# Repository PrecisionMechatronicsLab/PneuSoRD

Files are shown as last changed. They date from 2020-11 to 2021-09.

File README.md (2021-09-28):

<!-- TODO 
- Add image backgrounds
- Check the alternate text on images
- Add paypal link
 -->

# Overview
A link to the paper can be found here: http://www.precisionmechatronicslab.com/wp-content/uploads/2021/09/PneuSoRD_Paper_Submission.pdf

PneuSoRD is available to be purchased from: http://www.precisionmechatronicslab.com/soft-robotics/
<p align="center">
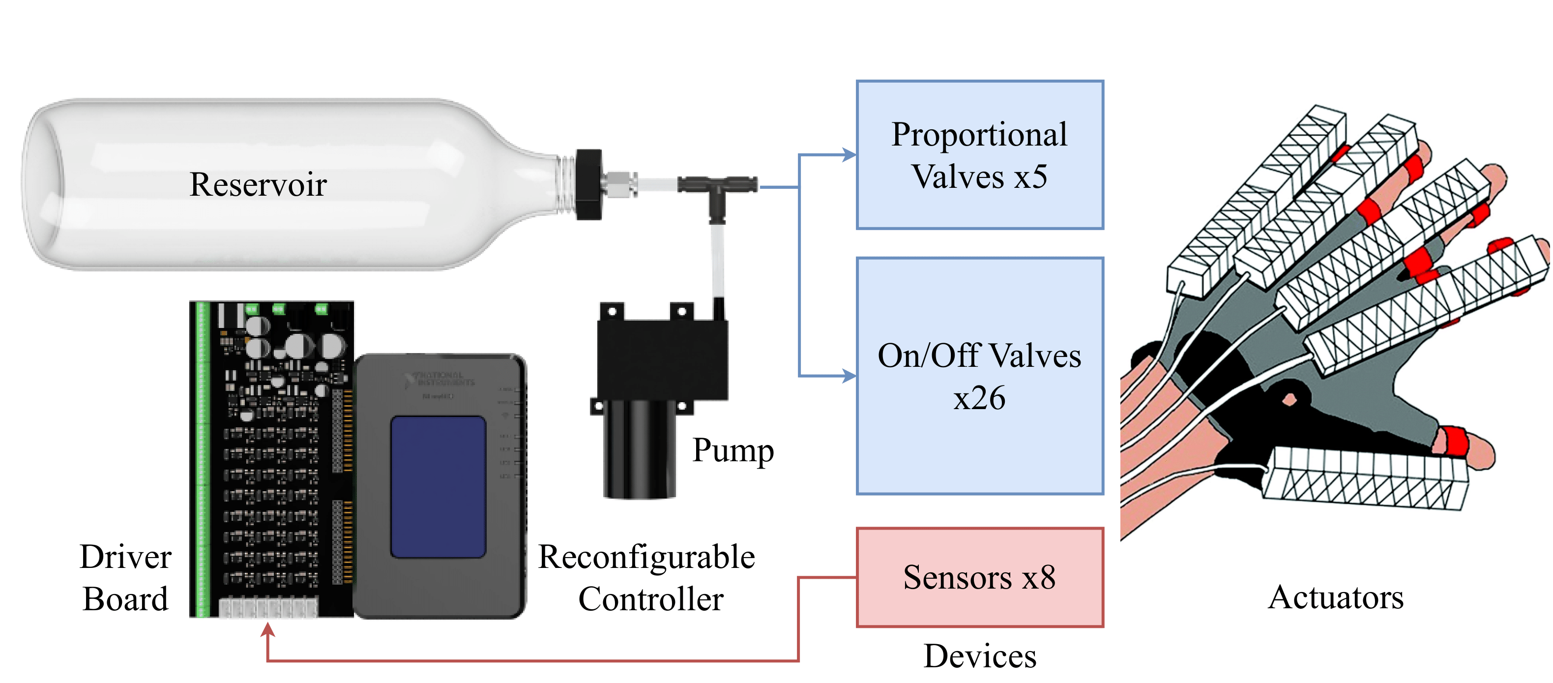
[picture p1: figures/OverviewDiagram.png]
Overview of the Pneumatic Soft Robotics Controller (PneuSoRD), including the electronics driver board and National Instruments myRIO controller, which is connected to a single pump and air receiver, up to 5 proportional valves, and 26 on-off valves. Soft robotic glove reproduced with permission fro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
	
</p>

The Pneumatic Soft Robotics Driver (PneuSoRD) is an open-source power electronics design for controlling pneumatic soft robotic actuators with a large number of simultaneous actuated chambers. This system is designed around the two major categories of valve types. On/Off valves with single or multiple solenoids which each take a binary input and proportional valves which can be driven from a variable DC voltage. Therefore, the PneuSoRD design encompasses a modular solution for each drive system: The "Proportional Drive" and the "On/Off Drive". Each module has been designed to be as generic as possible to allow control of a large range of valves with an available control strategy for each. These two modules can be driven by either a myRIO 1950 embedded controller through a real-time visual user interface with LabVIEW or an Arduino DUE.

**NOTE:** rev. 0.2 boards (unmarked revision) require the primary voltage input to be 7-12V. The secondary input can be used 7-25V.

## PneuSoRD Driver and Shield
The PneuSoRD can be replicated via the PCB_PneuSoRD files for use with the myRIO. An optional Arduino Due shield can also be made to adapt the PneuSoRD to an Arduino Due mirco controller.

<!-- TODO Add more information regarding build - brief summary of costs
Cost per unit for 20 units \~$160 -->

<!-- TODO Check these docs -->
https://github.com/PrecisionMechatronicsLab/PneuSoRD/blob/main/PCB_PneuSoRD/PCB_IC/PneuSoRD-BOM.xlsx
https://github.com/PrecisionMechatronicsLab/PneuSoRD/blob/main/PCB_DueAdapter/PCB_DueAdapterL2/Due-BOM.xlsx

# Quickstart Guide

The following guide is for the example [3 Way 2 Position](LabVIEW/3Way_2Position/OnOffControl_32Valve.vi) as seen in [On/Off 3/2](##On/Off-3/2).

### Step 1 - Pneumatic Connection
Connect the components as seen in Fig [On/Off 3/2](##On/Off-3/2). The specific fittings and components will vary depending on the valves and sensors used in your setup. 

### Step 2 - Pump/Valve Connections
Connect the two leads of the DC pump/motor to the Motor +- screw terminals.

For the 3/2 example connect the two leads of the valve to the +- of the desired channel, the example code utilises SO1, however this can be changed.

Connect the wall wart or power supply to the V2 power input of the driver via the DC barrel jack or the screw terminals. This supply should be selected based on the operating voltage of the motor/valves used. If these are the same, only one supply is needed, if they are different a second power supply can be connected to the V1 DC barrel jack or screw terminals. 

Using a pin jumper connect each devices controller to the appropriate power supply for that device. The right pin is used for V1 and the left for V2.

**NOTE:** rev. 0.2 boards (unmarked revision) require the primary voltage input to be 7-12V. The secondary input can be used 7-25V.

### Step 3 - Sensor Input
Connect the analogue sensor connectors to the headers marked AIX on the PCB.
For the example 3/2 on/off AI1 Pump, AI2 Actuator.

### Step 4 - LabVIEW Configuration
For each device configure the correct myRIO port.

Double clicking on the IO block for each device allows the user to configure the pin which the block reads/writes to and from. Set the pump, valve and sensors to use the myRIO pins which collorate to the driver pins. See tables [MXP A](#MXP-A) and [MXP B](#MXP-B) for the correct pin.

<p align="center">
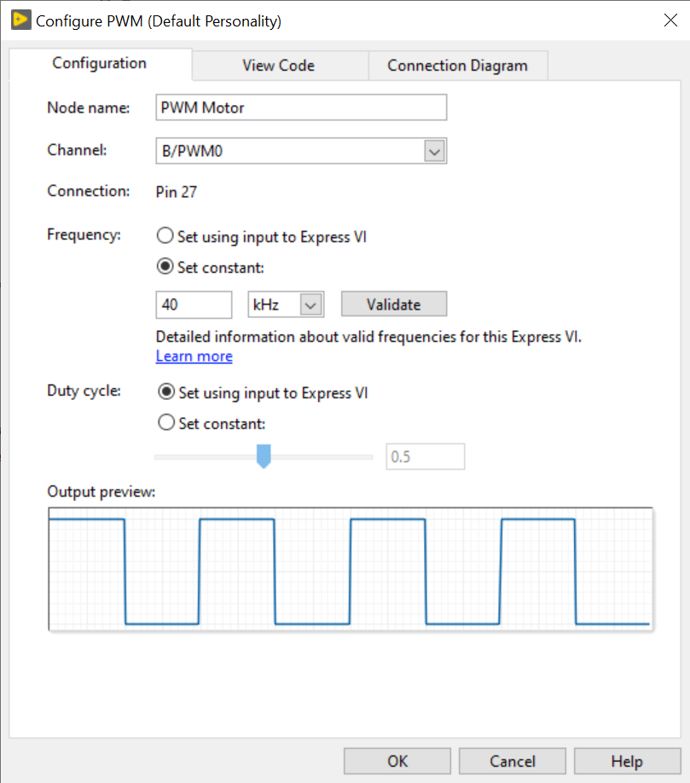
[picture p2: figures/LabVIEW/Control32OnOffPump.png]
LabView Control32OnOffPump interface
	
</p>

<p align="center">3/2 on-off pump configuration</p>

<p align="center">
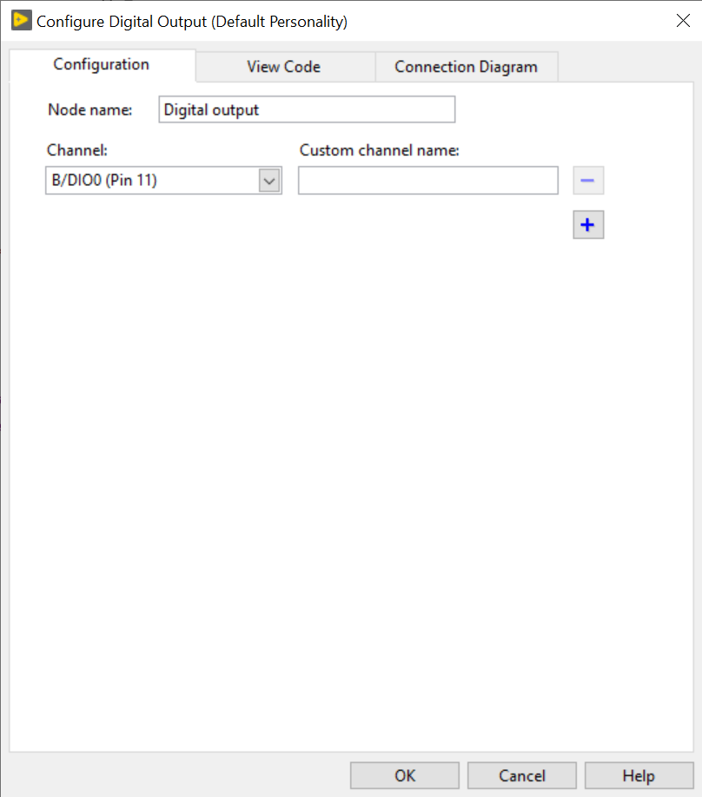
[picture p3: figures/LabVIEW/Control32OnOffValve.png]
LabView Control32OnOffValve interface
	
</p>

<p align="center">3/2 on-off valve configuration</p>

<p align="center">
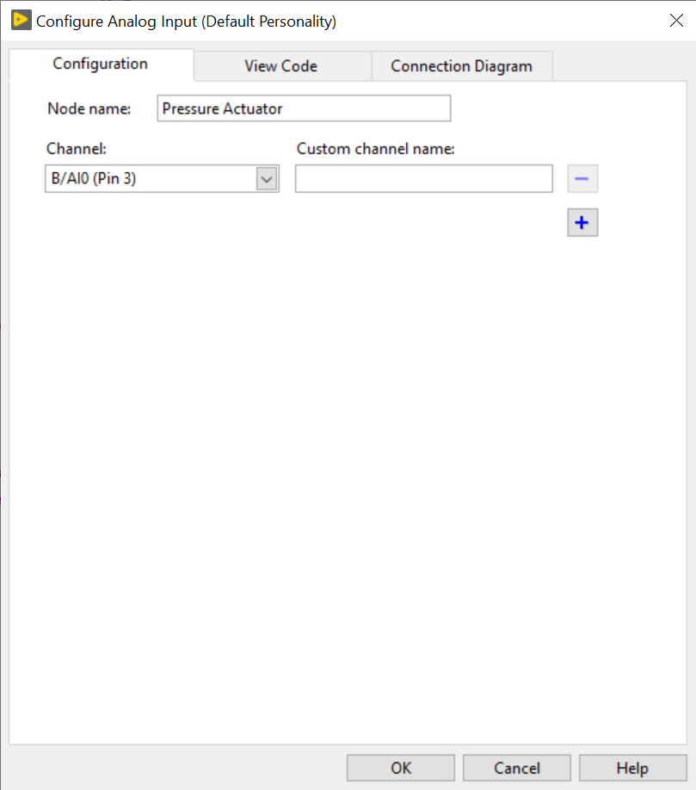
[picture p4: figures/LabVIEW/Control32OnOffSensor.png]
LabView Control32OnOffSensor interface
	
</p>

<p align="center">3/2 on-off sensor</p>

### Step 5 - Running the LabVIEW vi
Once the configuration is complete, the system is ready to test. Use the *run* and *Abort Execution* buttons to control the device. 

The "Setpoint Receiver" slider allows the resivour pressure (kPa) to be adjusted. The limit for this pressure is dependent on the resivour and pump used.

The second slider "Setpoint Actuator" adjusts the desired actuator pressure. 

For each slider there is an associated "Performance" guage. The *red* needle displays the setpoint direct from the slider and the *black* needle displays the measured pressure.

<!-- TODO Talk about the control view -->
<p align="center">
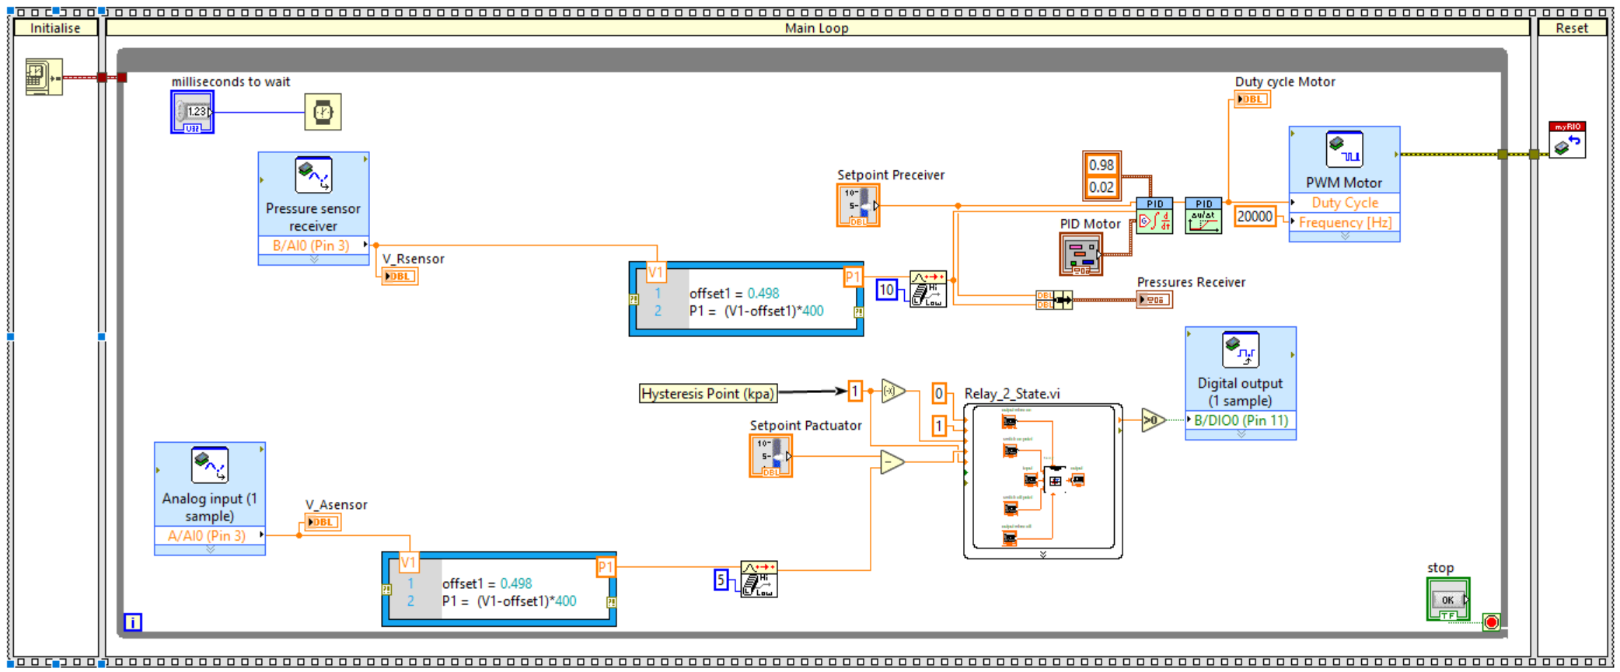
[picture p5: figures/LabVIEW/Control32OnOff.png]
	
</p>

<!-- TODO Talk about the interface view -->
<p align="center">
	LabView control interface 3/2 On/Off
</p>

Table of contents
=================
<!-- TODO Update TOC -->
<!--ts-->
   * [Overview](#Overview)
   * [Quickstart Guide](#Quickstart-Guide)
   * [PneuSoRD Driver](#PneuSoRD-Driver)
   * [Pnuematic Overview](#Pnuematic-Overview)
	 * [Pump/Compressor ](#Pump/Compressor )
	 * [3/2 Valve Configuration](#3/2-Valve-Configuration)
	 * [3/3 Valve Configuration](#3/3-Valve-Configuration)
	 * [2x 2/2 Valve Configuration](#2x-2/2-Valve-Configuration)
   * [LabVIEW Overview](#LabVIEW-Overview)
	 * [Main Loop](#Main-Loop)
	 * [Analog Input](#Analog-Input)
	 * [PWM](#PWM)
	 * [Simulated Squarewave](#Simulated-Squarewave)
	 * [Digital Write](#Digital-Write)
	 * [PID Block](#PID-Block)
	 * [Relay Block](#Relay-Block)
	 * [Rate Limiter Block](#Rate-Limiter-Block)
   * [Control Implementations](#Control-Implementations)
	 * [Pump Control](#Pump-Control)
	 * [On/Off 3/2](#On/Off-3/2)
		 * [Bang-Bang](#Bang-Bang)
		 * [PID](#PID)
	 * [On/Off 2x 2/2](##On/Off-2x-2/2)
		 * [Bang-Bang](#Bang-Bang)
		 * [PID](#PID)
	 * [Proportional 3/2](#Proportional-3/2)
	 * [Proportional 2x 2/2](#Proportional-2x-2/2)
   * [Hardware Overview](#Hardware-Overview)
	 * [Electrical Design (PneuSoRD)](#Electrical-Design-(PneuSoRD))
		 * [Motor/Proportional Drive](#Motor/Proportional-Drive)
		 * [On/Off Drive](#On/Off-Drive)
		 * [Sensor Input](#Sensor-Input)
	 *  [Arduino Sheild](#Arduino-Shield)
	 * [Pin Mapping](#Pin-Mapping)
		 * [MXP A](#MXP-A)
		 * [MXP B](#MXP-B)
<!--te-->

# Pnuematic Overview
An overview of pneumatic configurations.

## Pump/Compressor 
<p align="center">
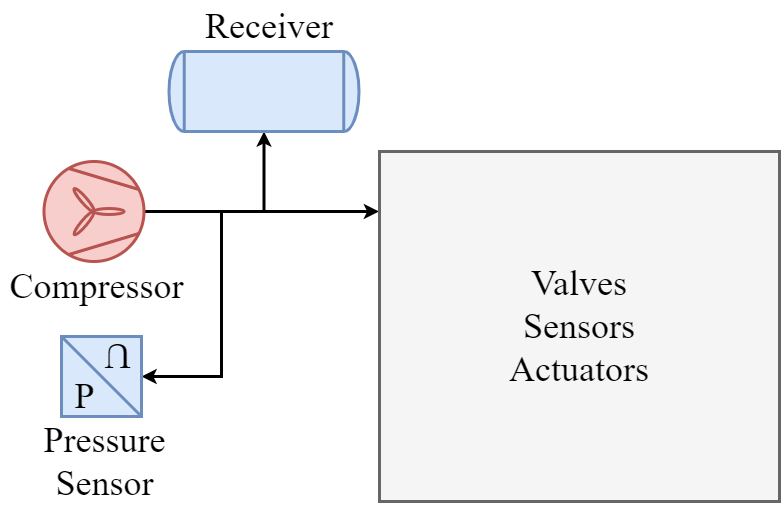
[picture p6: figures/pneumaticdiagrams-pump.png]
Air compressor with reservoir and pressure sensor
	
</p>

The main components of a compressed air system are the pump or source, an optional accumulator and an inline pressure sensor. The addition of an air receiver (storage reservoir or gas tank) to the pneumatic system smooths pulsating flow and prevents excessively temporary pressure drop during sudden short-term demand. Moreover, the air receiver allows for reduced energy consumption and fast pressurization of soft actuators.

## 3/2 Valve Configuration
<p align="center">
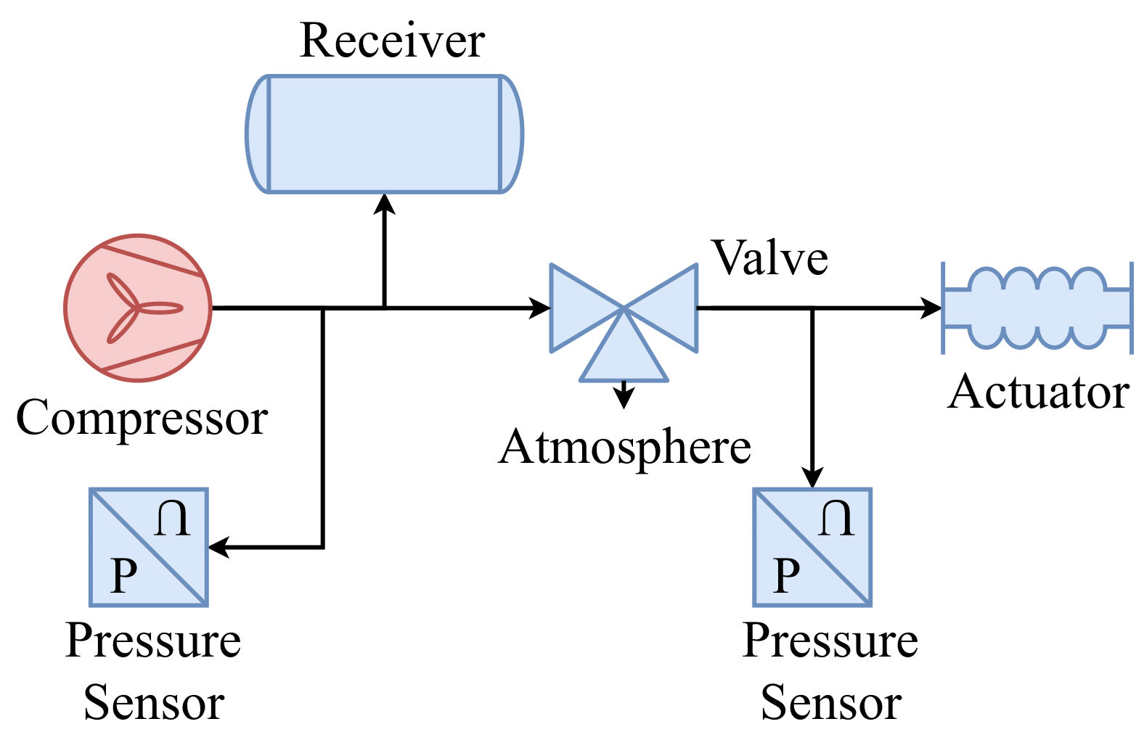
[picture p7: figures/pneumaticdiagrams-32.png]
Pneumatic system with a 3/2 valve coniguration
	
</p>

For the 3/2 valve system as shown above, the inlet port is connected to the compressor or the receiver, the outlet port is connected to the soft actuator and the exhaust port is open to atmosphere. The 3/2 valve system implies constantly inflating and deflating each pneumatic chamber, which causes the pressure in the actuator to continuously oscillate around its target and potentially reduces the lifetime of the valves.

## 3/3 Valve Configuration
<p align="center">
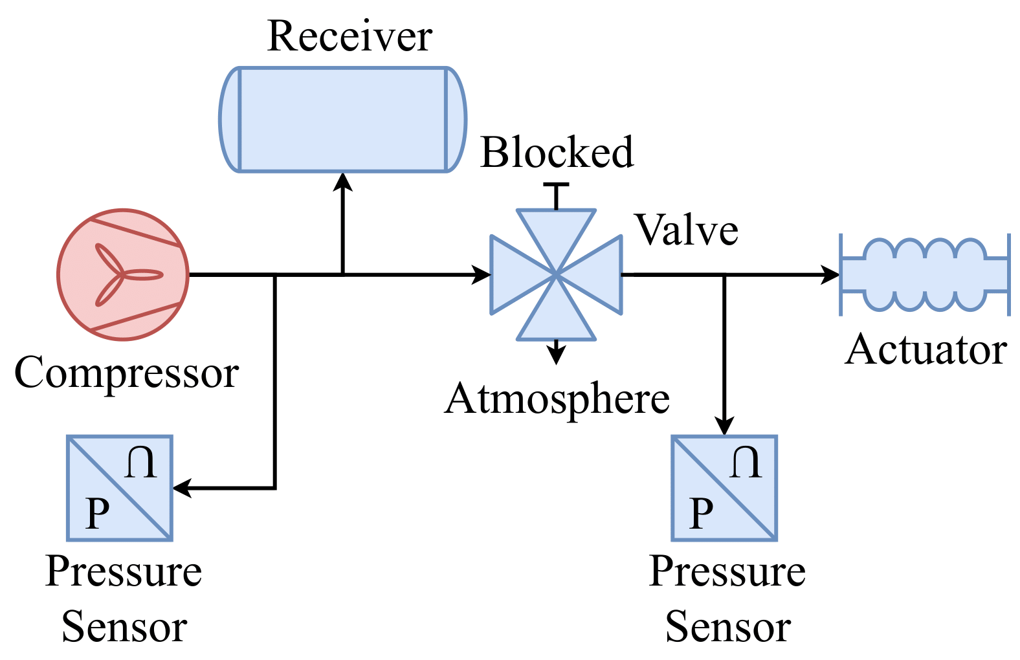
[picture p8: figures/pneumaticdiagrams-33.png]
Pneumatic system with a 3/3, 4/3 or 5/3 valve coniguration.
	
</p>

For the 3/3, 4/3 or 5/3 valve system as shown above, the inlet port is connected to the compressor or the receiver, the outlet port is connected to the soft actuator and the exhaust port is open to atmosphere. These valve systems have both inflating, deflating and holding modes.

## 2x 2/2 Valve Configuration
<p align="center">
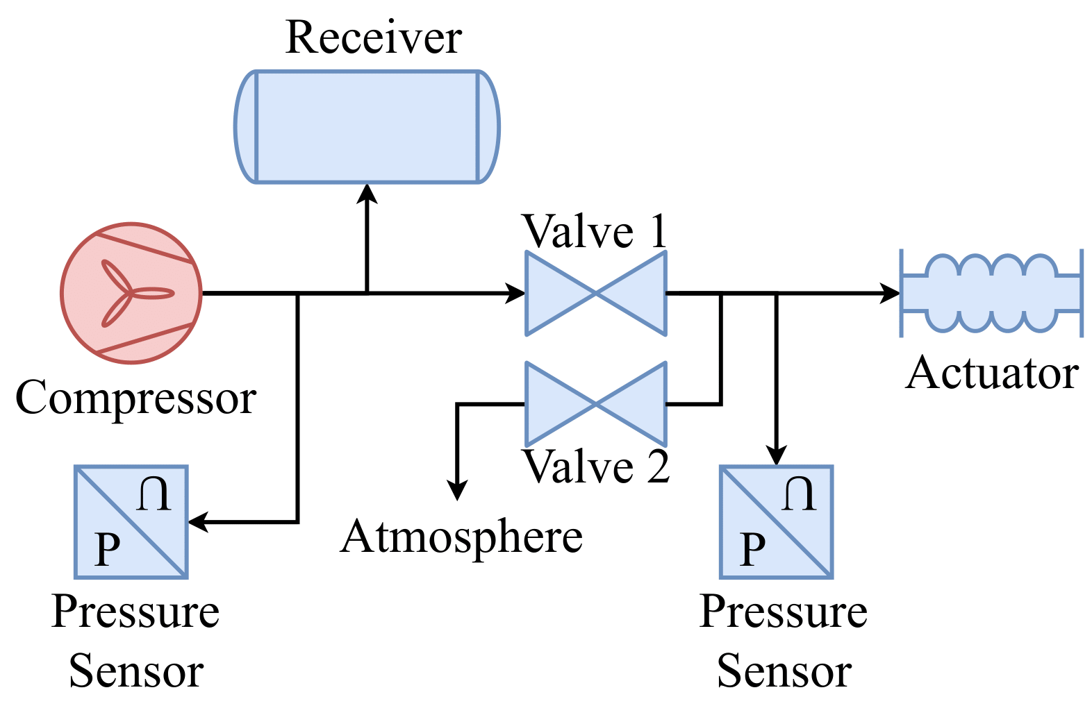
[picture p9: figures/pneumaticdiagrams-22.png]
Pneumatic system with 2x 2/2 valve coniguration
	
</p>

For the system with two 2/2 valves, the first valve is responsible for the charging process and has its inlet port connected to the compressor or the receiver and outlet port connected to the soft actuator. The second valve is responsible for the discharging process and has its inlet port connected to the soft actuator and outlet port open to atmosphere. Proportional valves outperform on-off solenoid valves in regards to tracking precision and steady-state accuracy but are 3-4 times more expensive.

# LabVIEW Overview
LabVIEW offers a graphical programming approach that helps you visualize every aspect of your application, including hardware configuration, measurement data, and debugging. This visualization makes it simple to design and develop custom engineering user interfaces.

Below is an overview of some of the major LabVIEW blocks used for a the outlined control configurations for the PneuSoRD.

## Installed packages

Download the 'LabVIEW 2019 myRIO Software Bundle' https://www.ni.com/en-au/support/downloads/software-products/download.labview-myrio-software-bundle.html and install these optional dependencies
-	JKI VI Package Manager
-	LabVIEW
-	LabVIEW myRIO Toolkit
-	LabVIEW Real-Time Module
-	LabVIEW Control Design and Simulation Module
-	LabVIEW MathScript Module
-	LabVIEW Robotics Module for LabRIO

## Main Loop
<p align="center">
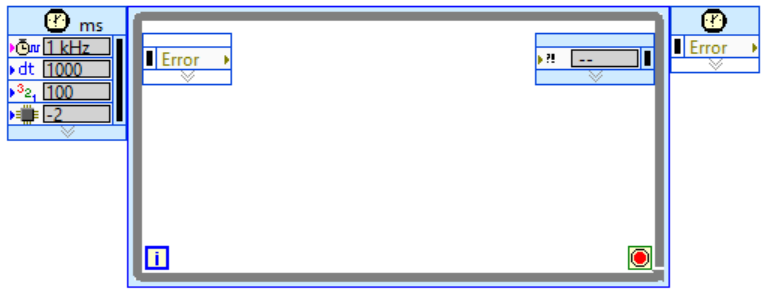
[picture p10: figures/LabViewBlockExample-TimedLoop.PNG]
LabView Timed Loop Block
	
</p>

The Timed Loop block  forms the foundation of the control system developed. All LabVIEW blocks are placed within this loop which determines the speed at which the control system runs. Whilst it is possible to replace this block with a While Loop, a fixed period is preferred. This block contains a parameter for setting the loop frequency or period.

## Analog Input
<p align="center">
	LabView Analog Input Block
</p>

This block reads the analog value of a single user predefined pin. This block contains no input functionality for use in the LabVIEW environment. The block outputs a 12bit analog value.

## PWM
<p align="center">
	LabView PWM Block
</p>

This block generates a hardware PWM signal to a single user predefined pin. The inputs to this block are the PWM duty cycle and PWM frequency. This block contains no output functionality for use in the LabVIEW environment.

## Simulated Squarewave
<p align="center">
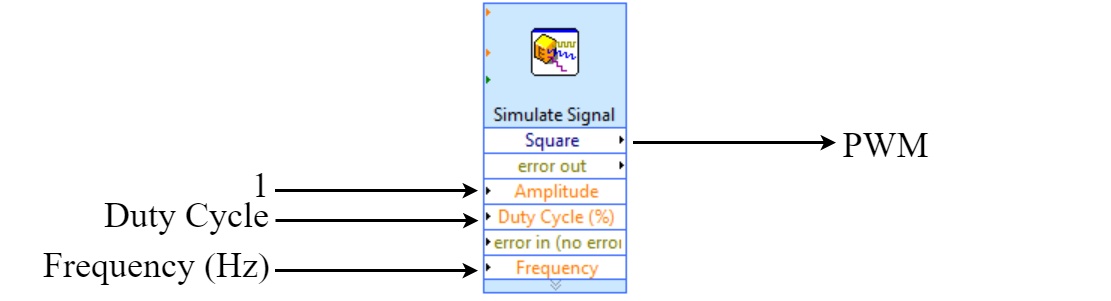
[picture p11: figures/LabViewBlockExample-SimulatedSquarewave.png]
LabView Simulated Squarewave Block
	
</p>

This block generates a wave function defined by the user. For this application a squarewave has been selected to mimic a PWM signal. The inputs to this block are the amplitude of the signal (for PWM generation this is 1), PWM duty cycle and PWM frequency. This block outputs the state of the Simulated wave at each loop itteration. 

## Digital Write
<p align="center">
	LabView Digital Write Block
</p>

This block allows the user to set the state of a single user predefined pin. The input to this block is the binary pin state. This block contains no output functionality for use in the LabVIEW environment. When used in conjunction with the Simulated Squarewave block this can be used to generate a software PWM signal.

## PID Block
<!-- TODO Add this image -->
<p align="center">
	LabView PID Block
</p>

This block implements a standard PID controller with P gain, I gain and D gain controls. The input to this block is the driving error signal. The output for this block is the driving control signal.

## Relay Block
<p align="center">
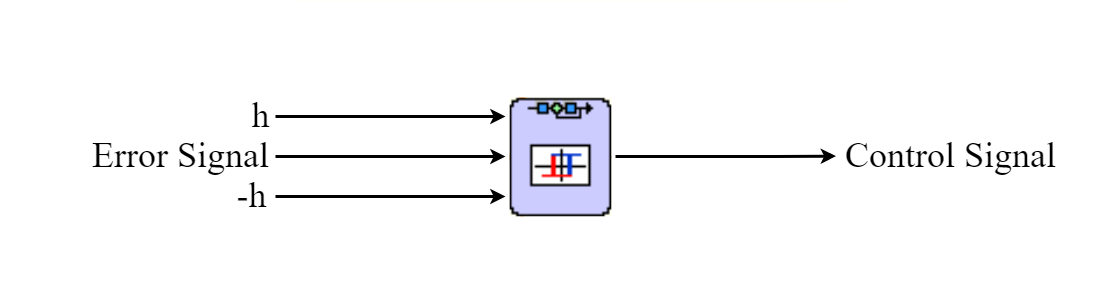
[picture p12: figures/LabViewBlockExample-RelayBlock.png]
LabView Relay Block
	
</p>

This block can be used to create a hysteresis window with two states. The inputs to this block are the maximum and minimum crossing point for the window and the driving error signal. The output to this block is the binary state of the signal.

<p align="center">
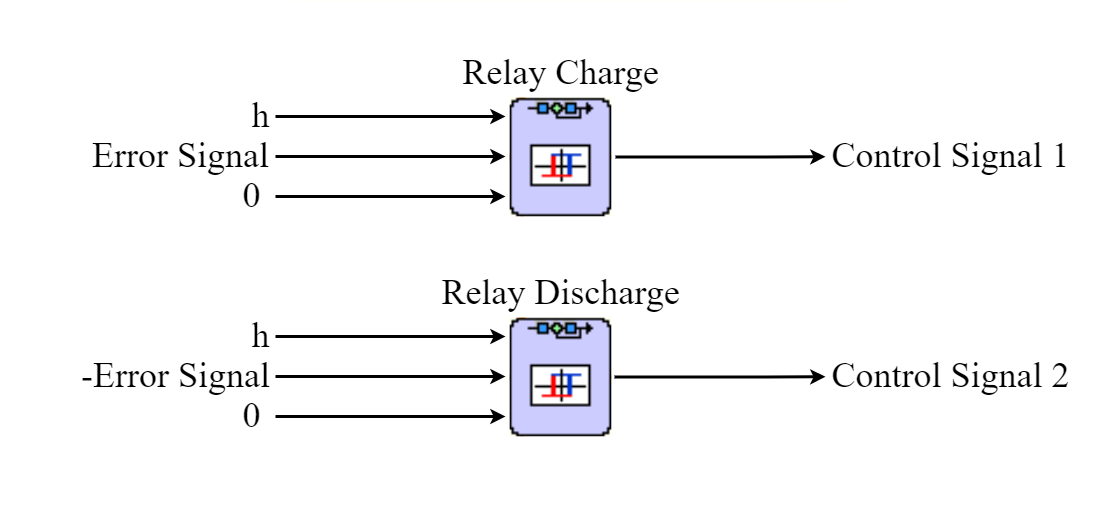
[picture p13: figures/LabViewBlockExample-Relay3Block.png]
LabView 3 State Relay Block
	
</p>

When combined with a second relay block, a three state hysteresis window can be implemented. The block inputs are the maximum, minimum and middle crossing point for the windows and the driving error signal. The output to this block is a pair of binary states for each window.

## Rate Limiter Block
<p align="center">
	LabView Rate Limiter Block
</p>

This block limits the rate of change over time of the input signal. The input to this block is the signal to be rate limited. The output to this block is the rate limited signal.

# Control Implementations
The following section decribes a control implementation for each valve type. Each of these control implementations are available in the repository above.

## Pump Control

The accumulator pressure requires closed-loop control to provide a constant source pressure. This is achieved by controlling the motor voltage by regulating the duty cycle using a PID controller.

<p align="center">
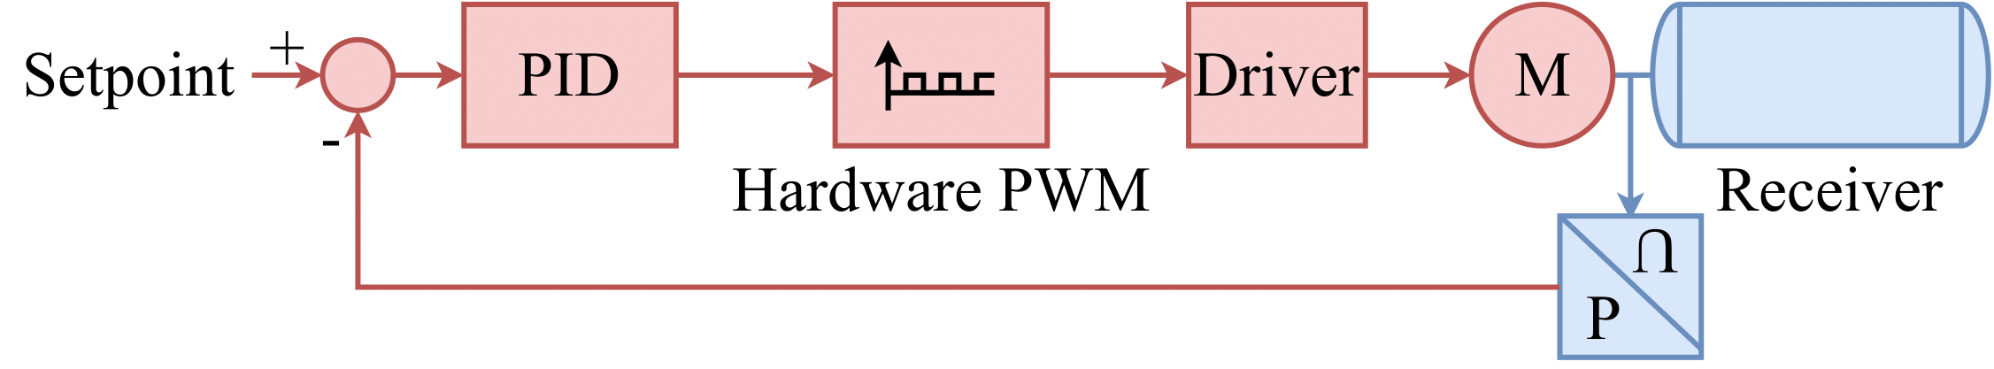
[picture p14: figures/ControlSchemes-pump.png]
Motor driver control scheme
	 
</p>

## On/Off 3/2
### Bang-Bang

For the system with a 3/2 on-off valve, the bang-bang controller is implemented with two states, which are:

<p align="center">
P < P_ref - h  
P > P_ref + h 
</p>

where **P** is the measured pressure, **P_ref** is the reference pressure and **h** is half the size of the hysteresis band. Lower values of hysteresis result in less steady-state error but also higher switching frequency. These conditions are implemented by using a relay block in Simulink or a relay function in a subsystem in LabVIEW with "switch on point" equal to **h** and "switch off point" equal to **-h**. Note that hysteresis is introduced for the bang-bang controllers to prevent excessive switching, which is particularly beneficial for the systems with 2/2 valves.

<p align="center">
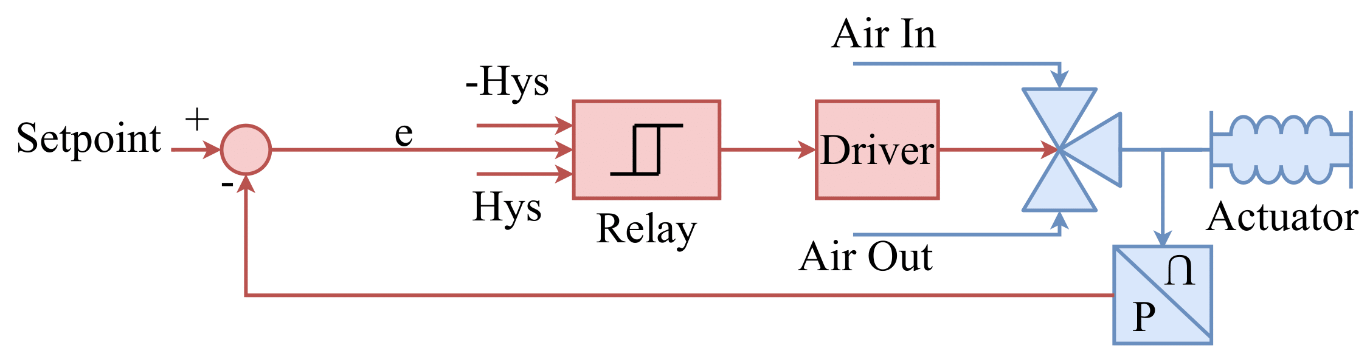
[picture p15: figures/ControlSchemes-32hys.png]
	 
</p>

### PID

For the system with a 3/2 on-off valve, the PID controller is implemented by regulating the duty cycle of the PWM wave into the valve between zero and 100%, which is used to switch the valve continuously between two states at a fixed frequency, e.g. 40Hz.

<p align="center">
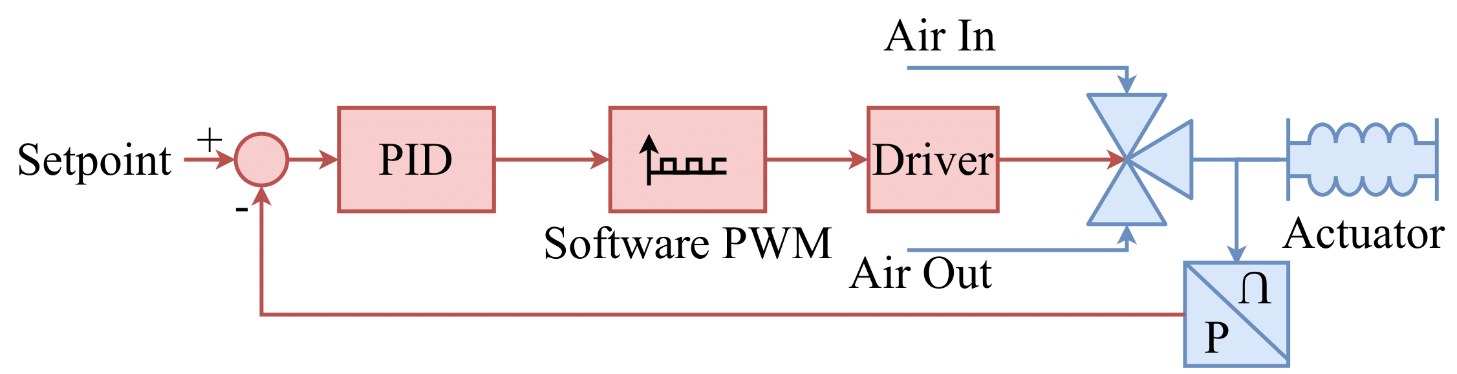
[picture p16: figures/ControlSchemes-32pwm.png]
3/2 on-off valve system with PID controller
	 
</p>

## On/Off 2x 2/2
For the system with two 2/2 on-off valves, the first valve (control **u_1**) is used for charging by allowing air flow from the receiver into the actuator. The second valve (control **u_2**) is used for discharging by allowing flow from the actuator into atmosphere.
### Bang-Bang

The bang-bang controller, three states can be used. In the first state, valve 1 is used for charging the actuator while valve 2 is blocked, i.e. **u_1 = 1** and **u_2 = 0**. In the second state, both valves are blocked and no flow is allowed from the receiver or into the atmosphere, i.e. **u_1 = 0** and **u_2 = 0**. Finally, in the third state, valve 2 is used to discharge the actuator into the atmosphere while valve 1 is blocked, i.e. **u_1 = 0** and **u_2 = 1**. These conditions can be implemented using a case structure (state machine) with three states or by considering the logic below with two relays.

Valve 1

* Switch on: P_ref - P > h

* Switch off: P_ref - P = 0

Valve 2

* Switch on: P_ref - P < -h

* Switch off: P_ref - P = 0

<p align="center">
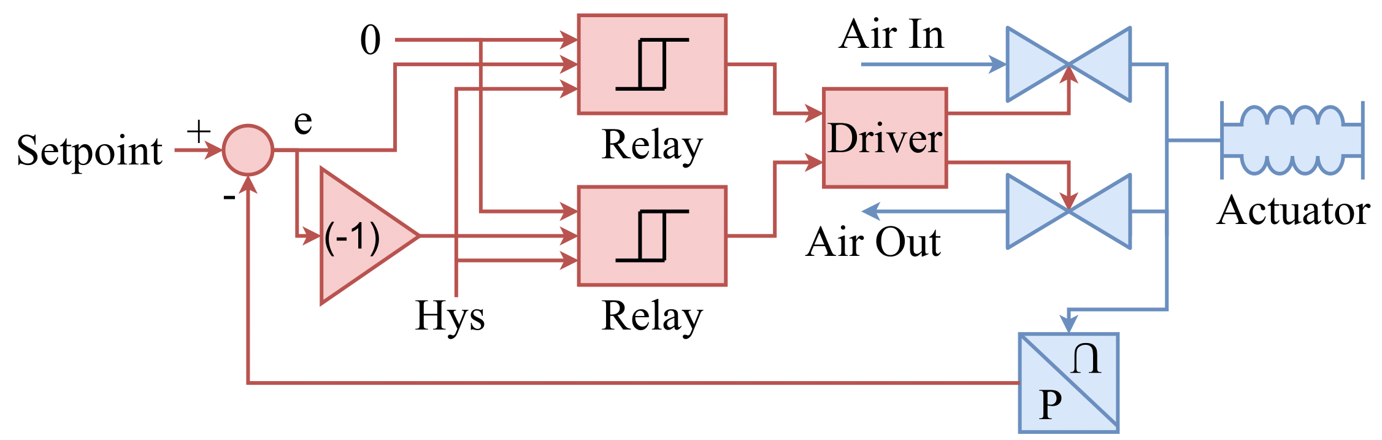
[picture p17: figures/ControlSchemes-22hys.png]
2x 2/2 on-off valve system with bang-bang controller
	 
</p>

### PID

The PID controller is implemented by regulating the duty cycle of complementary PWM signals at a fixed frequency.

<p align="center">
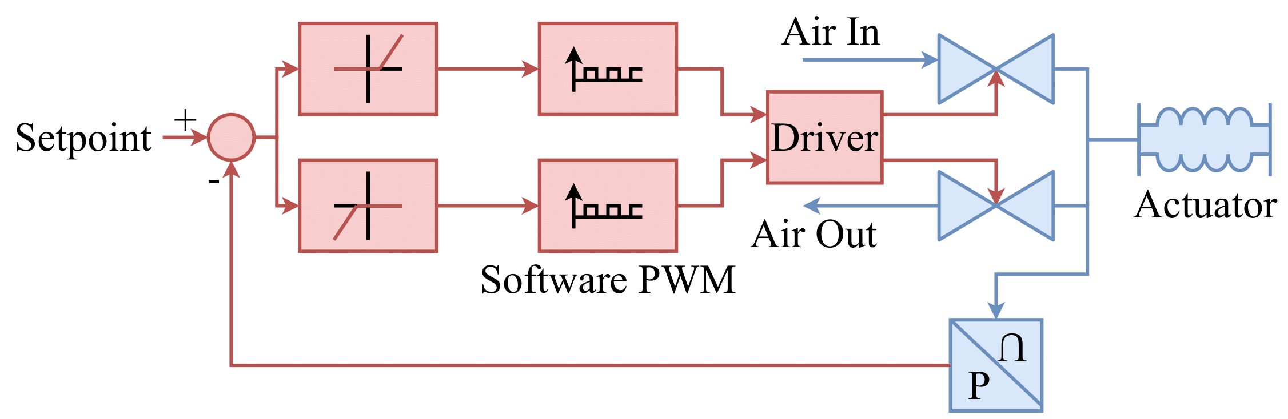
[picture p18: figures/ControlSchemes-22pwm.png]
2x 2/2 on-off valve system with PID controller
	 
</p>

## Proportional 2x 2/2

For 2/2 proportional valves, the mapping from input voltage to output flow is approximately linear over the operating range. A small deadband can be implemented for each valve around the zero error point. Outside of this region a linear mapping between error and duty cycle can be produced to regulate the pressure in the system. Alternatively, the use of a bang-bang controller would not be recommended, as this would effectively be treating the proportional valve as a two state on/off valve.

<p align="center">
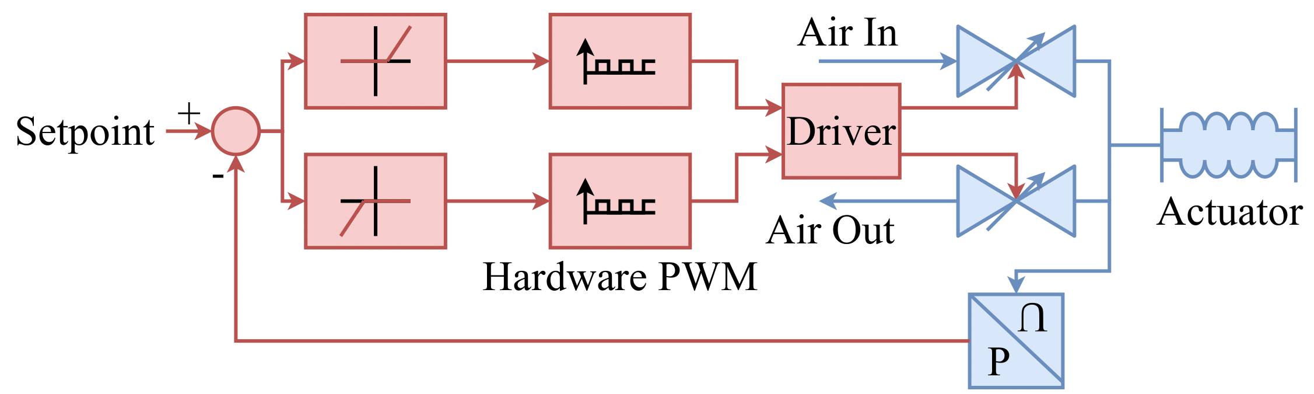
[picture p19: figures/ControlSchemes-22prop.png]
Proportional PWM driver with PID controller
	 
</p>

# Hardware Overview
The driver allows for the control of up to 31 valves for use in a multitude of applications. The number of sensor inputs is limited according the maximum number of analog inputs of myRIO. Consequently, 8 sensors input headers can be used to perform independent feedback control on 8 chambers. Note that more chambers can be actuated if they are allowed to share the same pressure values. 
An electrical PWM is used to drivethe proportional valves through a buck converter, which produces the required DC voltage. Where as a pneumatic PWM is produces by switching on and off the supply to the On/Off valves to produce the required driving signal. The PneuSoRD has two power inputs each of which can supply an operating voltage 7-25V. Two inputs were chosen to maximise the range or valves that could be driven. The primary input is used to power the 5V regulator and is required for the board's protection functionality. Whilst the secondary input is only required if a second voltage level is needed.

**NOTE:** rev. 0.2 boards (unmarked revision) require the primary voltage input to be 7-12V. The secondary input can be used 7-25V.

As seen in the image below, the driver interfaces with the myRIO via the two IDC connectors on the left hand side of the myRIO. 
<p align="center">
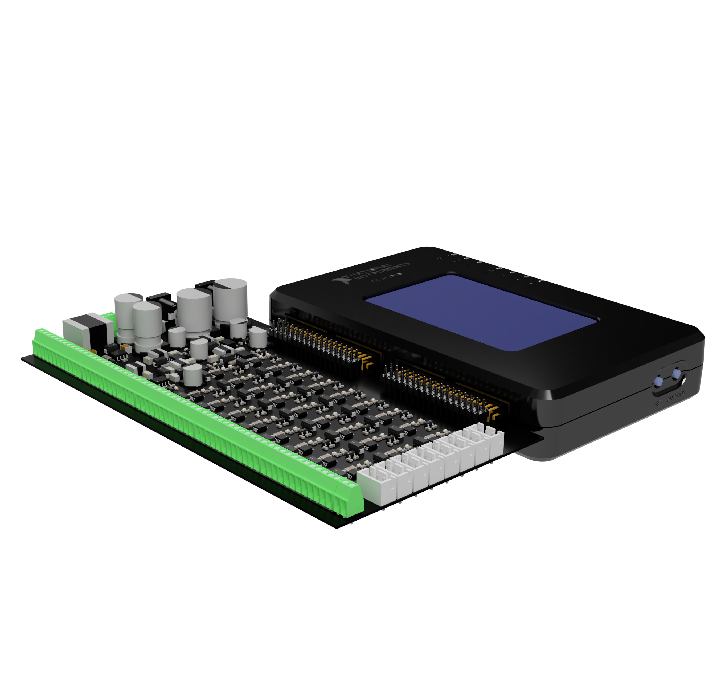
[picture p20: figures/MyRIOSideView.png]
MyRIO Side View
	
</p>

## Electrical Design (PneuSoRD)
Each module has been designed to maximise the variety of devices which can be driven. The following shows the implementation of the three drive designs and the feedback sensor electronics.  
<!-- <div class="text-red mb-2"> -->
Red - 26 On/Off Drives  
<!-- </div> -->
<!-- <div class="text-yellow mb-2"> -->
Yellow - 5 Proportional Drives
<!-- </div>   -->
<!-- <div class="text-blue mb-2"> -->
Blue - 1 Motor Drive  
<!-- </div> -->
<!-- <div class="text-green mb-2"> -->
Green - Power Supply  
<!-- </div> -->
<!-- <div class="text-orange mb-2"> -->
Orange - Sensor Inputs  
<!-- </div> -->
<!-- <div class="text-pink mb-2"> -->
Pink - Expansion Headers  
<!-- </div> -->

<p align="center">
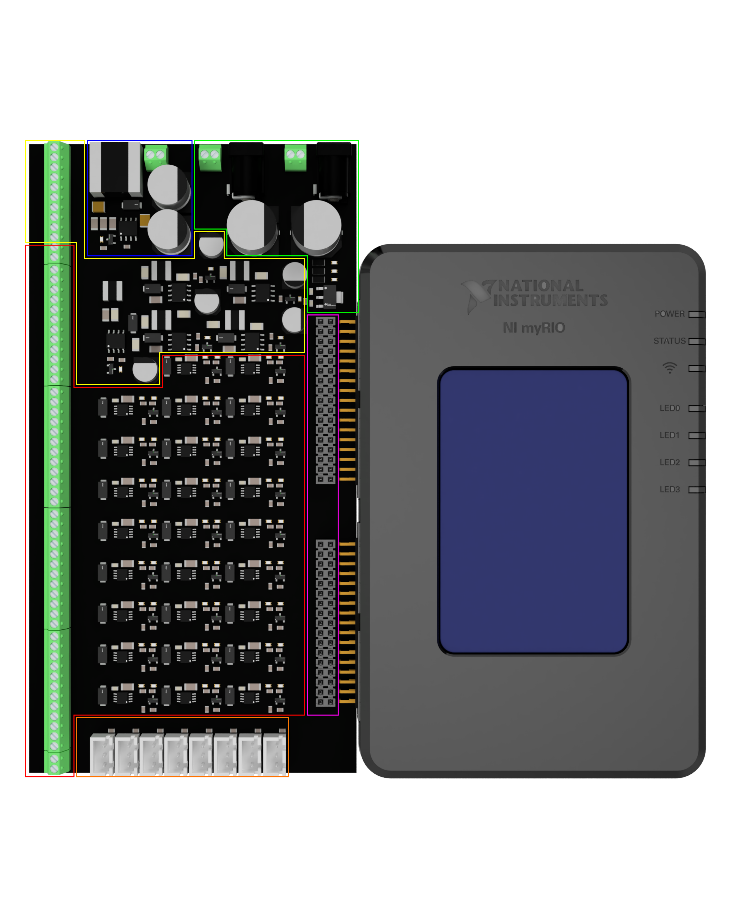
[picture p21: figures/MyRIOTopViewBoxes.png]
MyRIO Top View
	
</p>

### Motor/Proportional Drive
The PneuSoRD has 6 Proportional Drive modules. The motor driver is sized for a peak current up to 1.4A. This driver is designed for DC motor pumps that typically require a current of 500mA to 1A. This output could also be used to drive a logic signal for a larger pump. The 5 proportional drivers are sized for a peak current capacity up to 700mA. This driver is designed for driving proportional valves that typically require 200mA to 500mA.

The motor and proportional valve drivers are based off a synchronous rectifier buck converter. The switch is driven by a 40-200kHz PWM signal with a variable duty cycle, which can be generated by the myRIO or Arduino Due controllers. The switch (DRV88703.6A) is a half-bridge motor driver and was selected for the comprehensive overload protection, which is described in Section .

Each circuit channel can be supplied by either of two power supply inputs via a jumper on each circuit channel. The maximum output current is set by the **Rsen** resistor, which provides over-current and short-circuit protection. In the default configuration, the motor driver channel can supply 1.4A continuously and 2.5A peak, which is adjustable up to 3.6A. The remaining 5 proportional driver channels can supply 500mA continuously and 

### On/Off Drive
Since on-off valves can be driven by a digital signal, the PneuSoRD uses 26 digital pins on the myRIO and Arduino Due. The TPS1H000 is a fully protected single channel high-side power switch with an integrated power transistor. Each drive contains an adjustable current limit that can be adjusted via the **Rsen** resistor. This protection feature limits the inrush or overload current. The trip delay capacitor has been selected to minimise the trip time if a fault event occurs. A light emitting diode is connected to the fault pin, which provides user feedback during a fault condition.

Each drive channel can be supplied by either of the power supply inputs via a jumper on each channel. The on-off channels can supply 500mA continuously, with a peak of 500mA, which is adjustable up to 1A.

### Sensor Input
A total of 8 sensor input headers are included on the PneuSoRD, with an additional 4 included on the Arduino Due shield. A linear regulator provides each sensor with 5V, this reduces sensor noises caused by noise on the power rail due to the switching of the other components. Primarily, this input is designed for 0-5V sensors that can be read via the ADC input of the microcontroller. An optional resistor can be added to suit 4mA to 20mA style sensors.

## Arduino Shield
<!-- TODO add diagram of shield and overview -->
<p align="center">
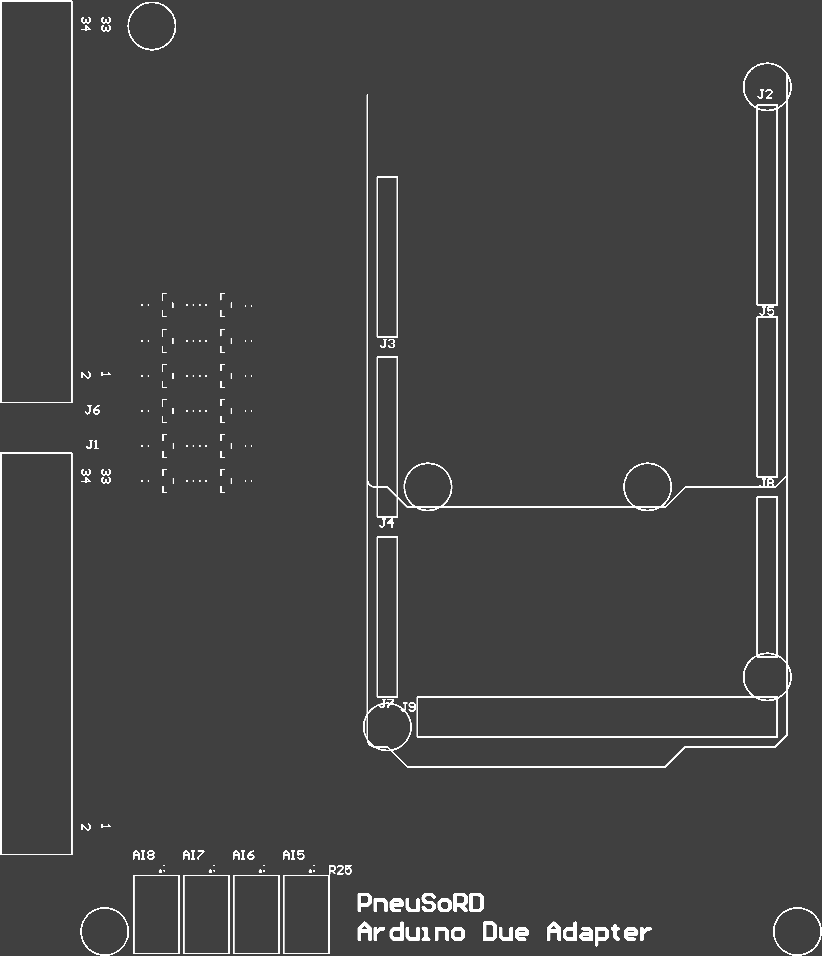
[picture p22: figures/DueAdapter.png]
Arduino Shield Render
	
</p>

## Pin Mapping
The pin mapping for the PneuSoRD integrates the two MXP connectors of the MyRIO. The table below presents the pin mapping as seen in the orientation of the PneuSoRD driver. This is also the orientation of the pins of the breakout header.

<p align="center">
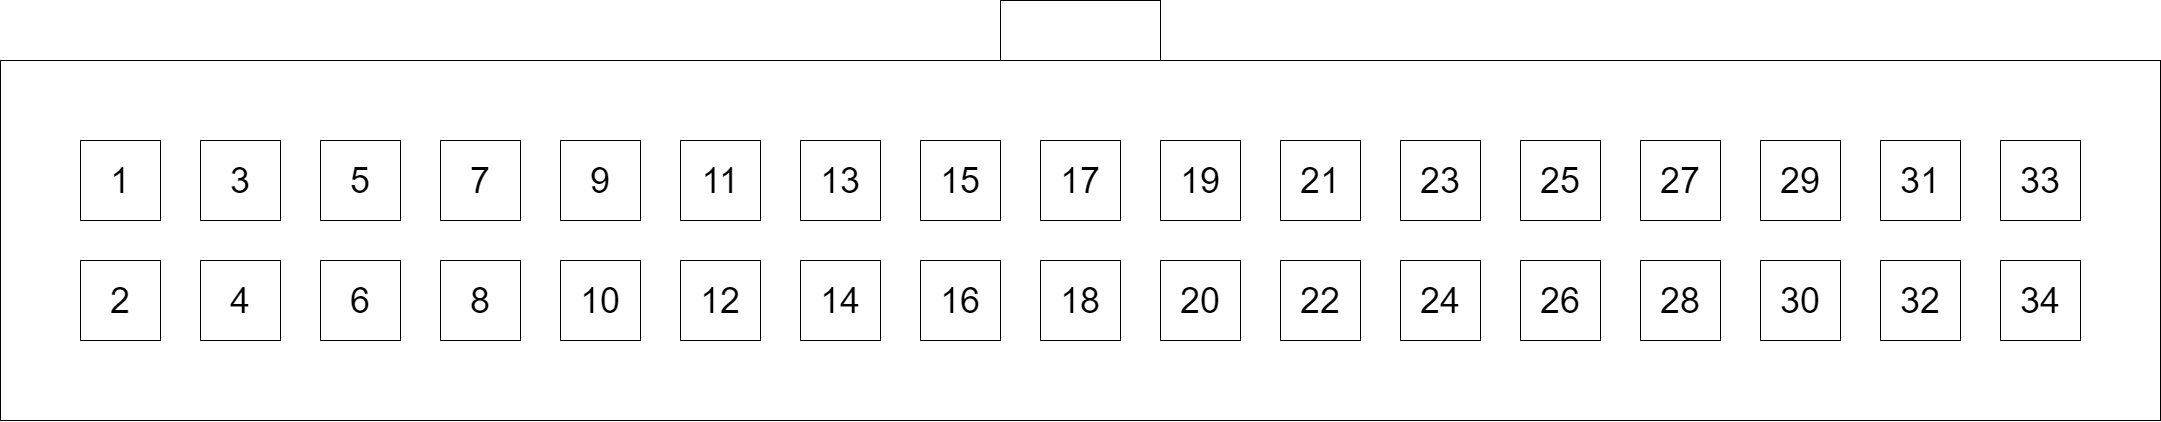
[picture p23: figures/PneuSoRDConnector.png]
MyRIO MXP Connector
	
</p>

### MXP A
| MyRIO Pin | MyRio Function | PneuSoRD Pin | MyRIO Pin | MyRio Function | PneuSoRD Pin | 
| ------ | ------ | ------ | ------ | ------ | ------ |
| MXP A Pin 34 | DIO15/I2C.SDA | SO26 | MXP A Pin 33 | +3.3V         | 3V3  |
| MXP A Pin 32 | DIO14/I2C.SCL | SO25 | MXP A Pin 31 | DIO10/PWM2    | P5   |
| MXP A Pin 30 | DGND          | GND  | MXP A Pin 29 | DIO9/PWM1     | P4   |
| MXP A Pin 28 | DGND          | GND  | MXP A Pin 27 | DIO8/PWM0     | P3   |
| MXP A Pin 26 | DIO13         | SO24 | MXP A Pin 25 | DIO7/SPI.MOSI | SO23 |
| MXP A Pin 24 | DGND          | GND  | MXP A Pin 23 | DIO6/SPI.MISO | SO22 |
| MXP A Pin 22 | DIO12/ENC.B   | SO21 | MXP A Pin 21 | DIO5/SPI.CLK  | SO20 |
| MXP A Pin 20 | DGND          | GND  | MXP A Pin 19 | DIO4          | SO19 |
| MXP A Pin 18 | DIO11/ENC.A   | SO18 | MXP A Pin 17 | DIO3          | SO17 |
| MXP A Pin 16 | DGND          | GND  | MXP A Pin 15 | DIO2          | SO16 |
| MXP A Pin 14 | UART.TX       | NC   | MXP A Pin 13 | DIO1          | SO15 |
| MXP A Pin 12 | DGND          | GND  | MXP A Pin 11 | DIO0          | SO14 |
| MXP A Pin 10 | UART.RX       | NC   | MXP A Pin 9  | AI3           | AI8  |
| MXP A Pin 8  | DGND          | GND  | MXP A Pin 7  | AI2           | AI7  |
| MXP A Pin 6  | AGND          | NC   | MXP A Pin 5  | AI1           | AI6  |
| MXP A Pin 4  | AO1           | NC   | MXP A Pin 3  | AI0           | AI5  |
| MXP A Pin 2  | AO0           | NC   | MXP A Pin 1  | +5V           | 5V   |

### MXP B
| MyRIO Pin | MyRio Function | PneuSoRD Pin | MyRIO Pin | MyRio Function | PneuSoRD Pin | 
| ------ | ------ | ------ | ------ | ------ | ------ |
| MXP B Pin 34 | DIO15/I2C.SDA | SO13 | MXP B Pin 33 | +3.3V         | 3V3  |
| MXP B Pin 32 | DIO14/I2C.SCL | SO12 | MXP B Pin 31 | DIO10/PWM2    | P2   |
| MXP B Pin 30 | DGND          | GND  | MXP B Pin 29 | DIO9/PWM1     | P1   |
| MXP B Pin 28 | DGND          | GND  | MXP B Pin 27 | DIO8/PWM0     | MTR  |
| MXP B Pin 26 | DIO13         | SO11 | MXP B Pin 25 | DIO7/SPI.MOSI | SO10 |
| MXP B Pin 24 | DGND          | GND  | MXP B Pin 23 | DIO6/SPI.MISO | SO09 |
| MXP B Pin 22 | DIO12/ENC.B   | SO08 | MXP B Pin 21 | DIO5/SPI.CLK  | SO07 |
| MXP B Pin 20 | DGND          | GND  | MXP B Pin 19 | DIO4          | SO06 |
| MXP B Pin 18 | DIO11/ENC.A   | SO05 | MXP B Pin 17 | DIO3          | SO04 |
| MXP B Pin 16 | DGND          | GND  | MXP B Pin 15 | DIO2          | SO03 |
| MXP B Pin 14 | UART.TX       | NC   | MXP B Pin 13 | DIO1          | SO02 |
| MXP B Pin 12 | DGND          | GND  | MXP B Pin 11 | DIO0          | SO01 |
| MXP B Pin 10 | UART.RX       | NC   | MXP B Pin 9  | AI3           | AI4  |
| MXP B Pin 8  | DGND          | GND  | MXP B Pin 7  | AI2           | AI3  |
| MXP B Pin 6  | AGND          | NC   | MXP B Pin 5  | AI1           | AI2  |
| MXP B Pin 4  | AO1           | NC   | MXP B Pin 3  | AI0           | AI1  |
| MXP B Pin 2  | AO0           | NC   | MXP B Pin 1  | +5V           | 5V   |

### Arduino Due Shield
| MCU Pin | Arduino Pin | PneuSoRD Pin |
| ------ | ------ | ------ |
| PA16 | A0  | A1    |
| PA24 | A1  | A2    |
| PA23 | A2  | A3    |
| PA22 | A3  | A4    |
| PA6  | A4  | A5    |
| PA4  | A5  | A6    |
| PA3  | A6  | A7    |
| PA2  | A7  | A8    |
|      |     |       |
| PB17 | A8  | \*A9  |
| PB18 | A9  | \*A10 |
| PB19 | A10 | \*A11 |
| PB20 | A11 | \*A12 |
| PB15 |     | NC    |
| PB16 |     | NC    |
| PA1  |     | NC    |
| PA0  |     | NC    |

\*Items on adapter PCB

| MCU Pin | Arduino Pin | PneuSoRD Pin | MCU Pin | Arduino Pin | PneuSoRD Pin |
| ------ | ------ | ------ | ------ | ------ | ------ |
| +5V  | +5V | NC   | +5V  | +5V | NC   |
| PB26 | D22 | SO1  | PA14 | D23 | SO2  |
| PA15 | D24 | SO3  | PD0  | D25 | SO4  |
| PD1  | D26 | SO5  | PD2  | D27 | SO6  |
| PD3  | D28 | SO7  | PD6  | D29 | SO8  |
| PD9  | D30 | SO9  | PA7  | D31 | SO10 |
| PD10 | D32 | SO11 | PC1  | D33 | SO12 |
| PC2  | D34 | SO13 | PC3  | D35 | P1   |
| PC4  | D36 | SO14 | PC5  | D37 | P2   |
| PC6  | D38 | SO15 | PC7  | D39 | P3   |
| PC8  | D40 | SO16 | PC9  | D41 | P4   |
| PA19 | D42 | P5   | PA20 | D43 | SO17 |
| PC19 | D44 | SO18 | PC18 | D45 | MTR  |
| PC17 | D46 | SO19 | PC16 | D47 | SO20 |
| PC15 | D48 | SO21 | PC14 | D49 | SO22 |
| PC13 | D50 | SO23 | PC12 | D51 | SO24 |
| PB21 | D52 | SO25 | PB14 | D53 | SO26 |
| GND  | GND | GND  | GND  | GND | GND  |

# Useful Links
Arduino PID Library - https://playground.arduino.cc/Code/PIDLibrary/

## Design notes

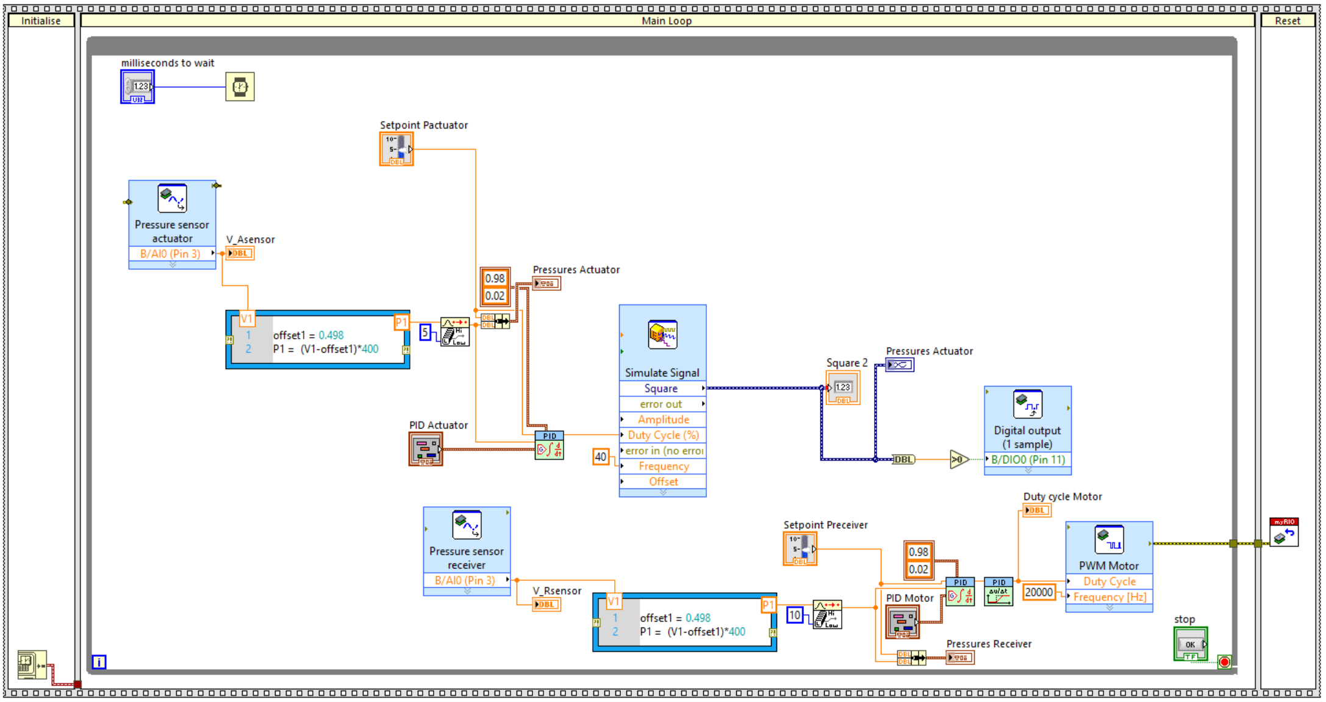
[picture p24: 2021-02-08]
figures/LabVIEW/Control32PID.png

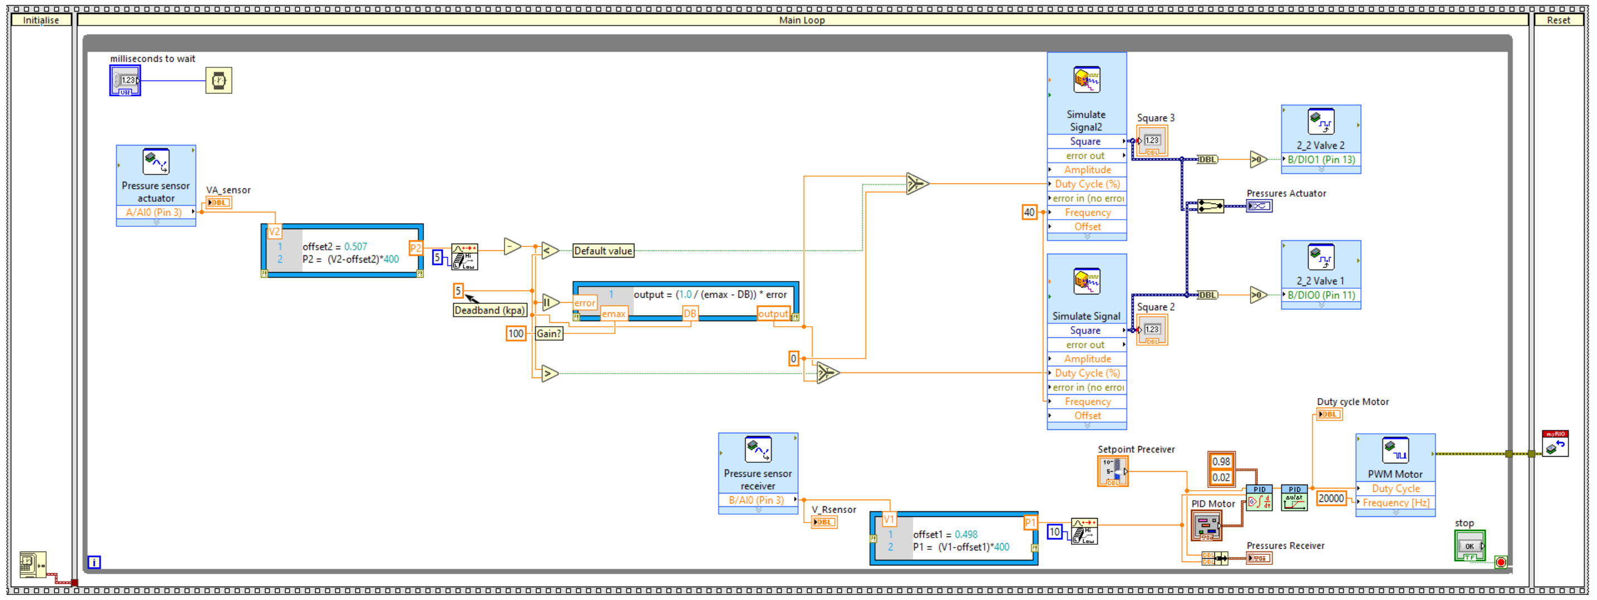
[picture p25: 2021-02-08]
figures/LabVIEW/Control22PID.png

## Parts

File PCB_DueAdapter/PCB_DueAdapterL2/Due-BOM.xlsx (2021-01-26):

 |  | Component list |  |  |  | Bill of Materials for PCB Document [PCB_IC.PcbDoc]
 |  | Source Data From: |  |  |  | PCB_IC.PcbDoc
 |  | Project: |  |  |  | PCB_IC.PrjPCB
 |  | Quantity |  |  |  | 20
 |  | Report Date: |  |  | 18/12/2020 | 10:52 AM
 |  |  |  |  |  |  | Data from Schematic |  | Ordered Part
# | Designator | Comment | Description | Footprint | LibRef | Quantity | Manufacturer | Manufacturer Part Number | Manufacturer | Manufacturer Part Number | # | Notes
1 | J1, J6 | 61203421721 | Male Box Header WR-BHD, THT, Angled, pitch 2.54 mm, 34 pins | 61203421721 | CMP-1502-00027-1 | 2 |  |  | Würth Elektronik | 61203421721 | 40
2 | J2 | Header10x1 |  | Header10x1 | Header10x1 | 1 |  |  | Samtec | ESQ-110-13-G-S | 20
3 | J3, J4, J5, J7, J8 | Header8x1 |  | Header8x1 | Header8x1 | 5 |  |  | Samtec | ESQ-108-13-G-S | 100
4 | J9 | Header18x2 |  | Header18x2 | Header18x2 | 1 |  |  | Samtec | ESQ-118-13-G-D | 20
5 | J10_Sens1, J10_Sens2, J10_Sens3, J10_Sens4 | B3B-XH-A(LF)(SN) | CONN HEADER VERT 3POS 2.5MM | FP-B3B-XH-A_LF_SN-MFG | CMP-17439-000014-1 | 4 |  |  | JST | B3B-XH-A(LF)(SN) | 80
6 | J11 | SSW-103-01-T-D | SQ Post Socket, Through-hole, Vertical, -55 to 105 degC, 2.54 mm Pitch, 6-Pin, Female, RoHS | SMTC-SSW-103-01-X-D | CMP-1023-00332-1 | 1 |  |  | Samtec | ESQ-103-13-G-D | 20
7 | Q1, Q2, Q3, Q4, Q5, Q6, Q7, Q8, Q9, Q10, Q11, Q12 | BSS138 | MOSFET N-CH 50V 220MA SOT-23 | FP-318-08-IPC_B | CMP-07173-000101-1 | 12 |  |  | ON Semiconductor | BSS138 | 240
8 | R1, R2, R3, R4, R5, R6, R7, R8, R9, R10, R11, R12, R13, R14, R15, R16, R17, R18, R19, R20, R21, R22, R23, R24 | 10K 1% 0603(1608) | 10K 0.1W 1% 0603 (1608 Metric) SMD | RESC0603(1608)_N | CMP-1012-00623-1 | 24 |  |  | Yageo | RC0603FR-0710KL | 480
9 | R25_Sens1, R25_Sens2, R25_Sens3, R25_Sens4 | 249R 1% 0603(1608) | 249R 0.1W 1% 0603 (1608 Metric) SMD | RESC0603(1608)_L | CMP-1012-00440-1 | 4 |  |  | DNP | DNP | 80

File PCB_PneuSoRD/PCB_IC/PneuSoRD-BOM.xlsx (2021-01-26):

 |  | Component list |  |  |  | Bill of Materials for PCB Document [PCB_IC.PcbDoc]
 |  | Source Data From: |  |  |  | PCB_IC.PcbDoc
 |  | Project: |  |  |  | PCB_IC.PrjPCB
 |  | Quantity |  |  |  | 100
 |  | Report Date: |  |  | 18/12/2020 | 10:52 AM
 |  |  |  |  |  |  | Data from Schematic |  | Ordered Part
# | Designator | Comment | Description | Footprint | LibRef | Quantity | Manufacturer | #Column Name Error:' Manufacturer Code | Manufacturer | 型号 | # | Notes | PN to quote
1 | C1, C3 | 100nF C-1206 | Ceramic 50V 1206 | C-1206 | C-1206 | 2 |  |  | Samsung | CL31B104KBCNFNC | 200 |  | CL31B104KBCNFNC
2 | C2, C4 | 220uF 50V Poly |  | CAPAE127P600-8N | C-Poly | 2 | AVX |  | Panasonic Electronic Components | EEH-ZS1H221P | 200 |  | EEHZS1H221P
3 | C5_OnOff1, C5_OnOff2, C5_OnOff3, C5_OnOff4, C5_OnOff5, C5_OnOff6, C5_OnOff7, C5_OnOff8, C5_OnOff9, C5_OnOff10, C5_OnOff11, C5_OnOff12, C5_OnOff13, C5_OnOff14, C5_OnOff15, C5_OnOff16, C5_OnOff17, C5_OnOff18, C5_OnOff19, C5_OnOff20, C5_OnOff21, C5_OnOff22, C5_OnOff23, C5_OnOff24, C5_OnOff25, C5_OnOff26 | CAP 10nF 50V 0603(1608) | CAP 10nF 50V ±20% 0603 (1608 Metric) Thickness 1mm SMD | CAPC0603(1608)100_L | CMP-1035-02322-1 | 26 |  |  | Samsung | CL10B103KB8NNNC | 2600 |  | CL10B103KB8NNNC
4 | C6 | CAP 330nF 35V 0603(1608) | CAP 330nF 35V ±10% 0603 (1608 Metric) Thickness 1mm SMD | CAPC0603(1608)100_L | CMP-1035-02677-1 | 1 |  |  | Samsung | CL10B333KB8NNNC | 100 |  | CL10B333KB8NNNC | 330nf or 33nF? 35v or 50V? | 330nF 50V
5 | C7 | CAP 1uF 35V 0603(1608) | CAP 1uF 35V ±10% 0603 (1608 Metric) Thickness 1mm SMD | CAPC0603(1608)100_L | CMP-1035-02743-1 | 1 |  |  | Samsung | CL10A105KB8NNNC | 100 |  | CL10A105KB8NNNC
6 | C9_Prop1, C9_Prop2, C9_Prop3, C9_Prop4, C9_Prop5 | 47uF 50V AuPoly |  | EEH-ZA1H220P | C-Poly | 5 | AVX |  | KEMET | EDH476M050A9HAA | 500 |  | EDH476M050A9HAA
7 | C10_Prop1, C10_Prop2, C10_Prop3, C10_Prop4, C10_Prop5, C11_Prop1, C11_Prop2, C11_Prop3, C11_Prop4, C11_Prop5 | CAP 10uF 50V 1206(3216) | CAP 10uF 50V ±20% 1206 (3216 Metric) Thickness 1.9mm SMD | CAPC1206(3216)190_N | CMP-1037-04983-1 | 10 |  |  | Samsung | CL31A106MBHNNNE | 1000 |  | CL31A106MBHNNNE
8 | C12, C13 | 470uF 50V AuPoly |  | CAPAE137130X163M | C-Poly | 2 | AVX |  | United Chemi-Con | EMVA500ARA471MKG5S | 200 |  | EMVA500ARA471MKG5S
9 | D1, D3_OnOff1, D3_OnOff2, D3_OnOff3, D3_OnOff4, D3_OnOff5, D3_OnOff6, D3_OnOff7, D3_OnOff8, D3_OnOff9, D3_OnOff10, D3_OnOff11, D3_OnOff12, D3_OnOff13, D3_OnOff14, D3_OnOff15, D3_OnOff16, D3_OnOff17, D3_OnOff18, D3_OnOff19, D3_OnOff20, D3_OnOff21, D3_OnOff22, D3_OnOff23, D3_OnOff24, D3_OnOff25, D3_OnOff26, D6, D7, D8, D9_Prop1, D9_Prop2, D9_Prop3, D9_Prop4, D9_Prop5 | 150060GS75000 | SMD mono-color Chip LED, WL-SMCW, Green | 0603_A | CMP-1426-00002-1 | 35 | Wuerth Elektronik |  | Lite-On Inc. | LTST-C191KGKT | 3500 |  |  | two part numbers,150060GS75000 and LTSTC191KGKT,please confirm which one is correct. | LTST-C191KGKT
10 | D2, D5_OnOff1, D5_OnOff2, D5_OnOff3, D5_OnOff4, D5_OnOff5, D5_OnOff6, D5_OnOff7, D5_OnOff8, D5_OnOff9, D5_OnOff10, D5_OnOff11, D5_OnOff12, D5_OnOff13, D5_OnOff14, D5_OnOff15, D5_OnOff16, D5_OnOff17, D5_OnOff18, D5_OnOff19, D5_OnOff20, D5_OnOff21, D5_OnOff22, D5_OnOff23, D5_OnOff24, D5_OnOff25, D5_OnOff26, D10_Prop1, D10_Prop2, D10_Prop3, D10_Prop4, D10_Prop5 | SK53A-LTP | DIODE SCHOTTKY 5A 30V SMA | FP-DO-214AC-MFG | CMP-56206-000004-1 | 32 |  |  | SMC Diode Solutions | SK34ATR | 3200 |  | SK34ATR
11 | D4_OnOff1, D4_OnOff2, D4_OnOff3, D4_OnOff4, D4_OnOff5, D4_OnOff6, D4_OnOff7, D4_OnOff8, D4_OnOff9, D4_OnOff10, D4_OnOff11, D4_OnOff12, D4_OnOff13, D4_OnOff14, D4_OnOff15, D4_OnOff16, D4_OnOff17, D4_OnOff18, D4_OnOff19, D4_OnOff20, D4_OnOff21, D4_OnOff22, D4_OnOff23, D4_OnOff24, D4_OnOff25, D4_OnOff26 | 150060RS75000 | SMD mono-color Chip LED, WL-SMCW, Red | 0603_A | CMP-1426-00001-1 | 26 | Wuerth Elektronik |  | Lite-On Inc. | LTST-C191KRKT | 2600 |  |  | LTST-C191KRKT or 150060RS75000? | LTST-C191KRKT
12 | J1, J9, J13, J14 | 1725656 | Male Header, Pitch 2.54 mm, 1 x 2 Position, Height 9 mm, Tail Length 3.5 mm | PHOE-1725656-2 | CMP-2000-05299-1 | 4 | Phoenix Contact |  | On Shore Technology Inc. | OSTVN02A150 | 400 |  |  | 1725656 or OSTVN02A150? | OSTVN02A150
13 | J2_Sens1, J2_Sens2, J2_Sens3, J2_Sens4, J2_Sens5, J2_Sens6, J2_Sens7, J2_Sens8 | B3B-XH-A(LF)(SN) | CONN HEADER VERT 3POS 2.5MM | FP-B3B-XH-A_LF_SN-MFG | CMP-17439-000014-1 | 8 | JST |  | JST | B3B-XH-A(LF)(SN) | 800 |  | B3B-XH-A(LF)(SN)
14 | J3, J10 | WE-CN-2P-F-R34 |  | 613034243121 | WE-CN-2P-F-R34 | 2 |  |  | Sullins Connector Solutions | SFH11-PBPC-D17-RA-BK | 200 |  | SFH11-PBPC-D17-RA-BK
15 | J4, J5, J6, J7, J8 | Phoenix Contact 1725753 |  | PHOE-1725656-12 | 1725753 | 5 |  |  | On Shore Technology Inc. | OSTVN12A150 | 500 |  | OSTVN12A150 | 1725753 or OSTVN12A150? | OSTVN12A150
16 | J11, J12 | PJ-102A | CONN PWR JACK 2X5.5MM SOLDER | FP-PJ-102A-MFG | CMP-14830-000006-1 | 2 | CUI |  | CUI Devices | PJ-102AH | 200 |  | PJ-102AH
17 | L1 | 470uH |  | L1212 | Inductor1212 | 1 | Wuerth Elektronik |  | Wuerth Elektronik | 7447709471 | 100 |  | 7447709471
18 | L2_Prop1, L2_Prop2, L2_Prop3, L2_Prop4, L2_Prop5 | 100uH |  | L0404 | Inductor0404 | 5 | Wuerth Elektronik |  | Laird-Signal Integrity Products | TYS5040101M-10 | 500 |  | TYS5040101M-10
19 | P1, P2_OnOff1, P2_OnOff2, P2_OnOff3, P2_OnOff4, P2_OnOff5, P2_OnOff6, P2_OnOff7, P2_OnOff8, P2_OnOff9, P2_OnOff10, P2_OnOff11, P2_OnOff12, P2_OnOff13, P2_OnOff14, P2_OnOff15, P2_OnOff16, P2_OnOff17, P2_OnOff18, P2_OnOff19, P2_OnOff20, P2_OnOff21, P2_OnOff22, P2_OnOff23, P2_OnOff24, P2_OnOff25, P2_OnOff26, P3_Prop1, P3_Prop2, P3_Prop3, P3_Prop4, P3_Prop5 | Header 3 | Header, 3-Pin | HDR1X3 | Header 3 | 32 |  |  | Würth Elektronik | 61300311121 | 3200 |  | 61300311121
20 | P4, P5 | PHT-117-01-L-D |  | PHT-117-01-L-D | PHT-117-01-L-D | 2 |  |  | Würth Elektronik | 61303421121 | 200 |  | 61303421121 | 61303421121 or PHT-117-01-L-D? | 61303421121
21 | Q1, Q2_OnOff1, Q2_OnOff2, Q2_OnOff3, Q2_OnOff4, Q2_OnOff5, Q2_OnOff6, Q2_OnOff7, Q2_OnOff8, Q2_OnOff9, Q2_OnOff10, Q2_OnOff11, Q2_OnOff12, Q2_OnOff13, Q2_OnOff14, Q2_OnOff15, Q2_OnOff16, Q2_OnOff17, Q2_OnOff18, Q2_OnOff19, Q2_OnOff20, Q2_OnOff21, Q2_OnOff22, Q2_OnOff23, Q2_OnOff24, Q2_OnOff25, Q2_OnOff26, Q3_Prop1, Q3_Prop2, Q3_Prop3, Q3_Prop4, Q3_Prop5 | BC846BLT3G | TRANS NPN 65V 0.1A SOT-23 | FP-318-08-IPC_C | CMP-07170-000022-1 | 32 |  |  | ON Semiconductor | BC846BLT3G | 3200 |  | BC846BLT3G
22 | R1, R6_OnOff1, R6_OnOff2, R6_OnOff3, R6_OnOff4, R6_OnOff5, R6_OnOff6, R6_OnOff7, R6_OnOff8, R6_OnOff9, R6_OnOff10, R6_OnOff11, R6_OnOff12, R6_OnOff13, R6_OnOff14, R6_OnOff15, R6_OnOff16, R6_OnOff17, R6_OnOff18, R6_OnOff19, R6_OnOff20, R6_OnOff21, R6_OnOff22, R6_OnOff23, R6_OnOff24, R6_OnOff25, R6_OnOff26, R9_OnOff1, R9_OnOff2, R9_OnOff3, R9_OnOff4, R9_OnOff5, R9_OnOff6, R9_OnOff7, R9_OnOff8, R9_OnOff9, R9_OnOff10, R9_OnOff11, R9_OnOff12, R9_OnOff13, R9_OnOff14, R9_OnOff15, R9_OnOff16, R9_OnOff17, R9_OnOff18, R9_OnOff19, R9_OnOff20, R9_OnOff21, R9_OnOff22, R9_OnOff23, R9_OnOff24, R9_OnOff25, R9_OnOff26, R15_Prop1, R15_Prop2, R15_Prop3, R15_Prop4, R15_Prop5 | 510R 5% 0603(1608) | 510R 0.1W 5% 0603 (1608 Metric) SMD | RESC0603(1608)_L | CMP-1012-00067-1 | 58 |  |  | Yageo | RC0603FR-07510RL | 5800 |  | RC0603FR-07510RL
23 | R2, R7_OnOff1, R7_OnOff2, R7_OnOff3, R7_OnOff4, R7_OnOff5, R7_OnOff6, R7_OnOff7, R7_OnOff8, R7_OnOff9, R7_OnOff10, R7_OnOff11, R7_OnOff12, R7_OnOff13, R7_OnOff14, R7_OnOff15, R7_OnOff16, R7_OnOff17, R7_OnOff18, R7_OnOff19, R7_OnOff20, R7_OnOff21, R7_OnOff22, R7_OnOff23, R7_OnOff24, R7_OnOff25, R7_OnOff26, R8_OnOff1, R8_OnOff2, R8_OnOff3, R8_OnOff4, R8_OnOff5, R8_OnOff6, R8_OnOff7, R8_OnOff8, R8_OnOff9, R8_OnOff10, R8_OnOff11, R8_OnOff12, R8_OnOff13, R8_OnOff14, R8_OnOff15, R8_OnOff16, R8_OnOff17, R8_OnOff18, R8_OnOff19, R8_OnOff20, R8_OnOff21, R8_OnOff22, R8_OnOff23, R8_OnOff24, R8_OnOff25, R8_OnOff26, R16_Prop1, R16_Prop2, R16_Prop3, R16_Prop4, R16_Prop5 | 10K 1% 0603(1608) | 10K 0.1W 1% 0603 (1608 Metric) SMD | RESC0603(1608)_N | CMP-1012-00623-1 | 58 |  |  | Yageo | RC0603FR-0710KL | 5800 |  | RC0603FR-0710KL
24 | R3, R4, R5, R17_Prop1, R17_Prop2, R17_Prop3, R17_Prop4, R17_Prop5 | 1R2 5% 1206(3216) | 1R2 0.25W 5% 1206 (3216 Metric) SMD | RESC1206(3216)_N | CMP-1014-00004-1 | 8 |  |  | Yageo | RC1206FR-071R2L | 800 |  | RC1206FR-071R2L
25 | R10_OnOff1, R10_OnOff2, R10_OnOff3, R10_OnOff4, R10_OnOff5, R10_OnOff6, R10_OnOff7, R10_OnOff8, R10_OnOff9, R10_OnOff10, R10_OnOff11, R10_OnOff12, R10_OnOff13, R10_OnOff14, R10_OnOff15, R10_OnOff16, R10_OnOff17, R10_OnOff18, R10_OnOff19, R10_OnOff20, R10_OnOff21, R10_OnOff22, R10_OnOff23, R10_OnOff24, R10_OnOff25, R10_OnOff26 | 953R 1% 1206(3216) | 953R 0.25W 1% 1206 (3216 Metric) SMD | RESC1206(3216)_L | CMP-1014-00508-1 | 26 |  |  | Yageo | RC1206FR-07953RL | 2600 |  | RC1206FR-07953RL
26 | R11 | 5K49 1206 | 0.25W 1206 | R-1206 | R-1206 | 1 |  |  | Yageo | RC1206FR-075K49L | 100 |  | RC1206FR-075K49L
27 | R12 | 750R 1206 | 0.25W 1206 | R-1206 | R-1206 | 1 |  |  | Yageo | RC1206FR-07750RL | 100 |  | RC1206FR-07750RL
28 | R13 | 2K49 1206 | 0.25W 1206 | R-1206 | R-1206 | 1 |  |  | Yageo | RC1206FR-072K49L | 100 |  | RC1206FR-072K49L
29 | R14_Sens1, R14_Sens2, R14_Sens3, R14_Sens4, R14_Sens5, R14_Sens6, R14_Sens7, R14_Sens8 | 249R 1% 0603(1608) | 249R 0.1W 1% 0603 (1608 Metric) SMD | RESC0603(1608)_L | CMP-1012-00440-1 | 8 |  |  | DNP | DNP | 800
30 | U1, U4_Prop1, U4_Prop2, U4_Prop3, U4_Prop4, U4_Prop5 | DRV8870 |  | SOIC127P600X170_HS-9N | DRV8870 | 6 |  |  | Texas Instruments | DRV8870DDAR | 600 |  | DRV8870DDAR
31 | U2_OnOff1, U2_OnOff2, U2_OnOff3, U2_OnOff4, U2_OnOff5, U2_OnOff6, U2_OnOff7, U2_OnOff8, U2_OnOff9, U2_OnOff10, U2_OnOff11, U2_OnOff12, U2_OnOff13, U2_OnOff14, U2_OnOff15, U2_OnOff16, U2_OnOff17, U2_OnOff18, U2_OnOff19, U2_OnOff20, U2_OnOff21, U2_OnOff22, U2_OnOff23, U2_OnOff24, U2_OnOff25, U2_OnOff26 | TPS1H000 |  | TSOP65P490X110_HS-9N | TPS1H000 | 26 |  |  | Texas Instruments | TPS1H000AQDGNRQ1 | 2600 |  | TPS1H000AQDGNRQ1
32 | U3 | UA78M05CDCYR | IC REG LINEAR 5V 500MA SOT223-4 | FP-DCY0004A-MFG | CMP-04917-000015-1 | 1 | Texas Instruments |  | Texas Instruments | UA78M05CDCYR | 100 |  | UA78M05CDCYR
 |  |  |  |  |  | 429
 | Other Components for PCB
100 | Jumper |  |  |  |  | 32 |  |  | Sullins Connector Solutions | QPC02SXGN-RC | 3200 |  | QPC02SXGN-RC
101 | AC Adapter |  |  |  |  | 2 |  |  | Tri-Mag, LLC | 888993000 | 200 |  | 888993000
102 | 12V Wall Adapter |  |  |  |  | 1 |  |  | Tri-Mag, LLC | ICM60-120 | 100 |  | ICM60-120
103 | 24V Wall Adapter |  |  |  |  | 1 |  |  | Tri-Mag, LLC | ICM60-240 | 100 |  | ICM60-240
104 | Sensor Plug |  |  |  |  | 8 |  |  | JST Sales America Inc. | XHP-3 | 800 |  | XHP-3
105 | Sensor Plug Crimp |  |  |  |  | 24 |  |  | JST Sales America Inc. | SXH-001T-P0.6 | 2400 |  | SXH-001T-P0.6
106 | Standoff |  |  |  |  | 4 |  |  | Essentra Components | MTS-10 | 400 |  | MTS-10
107 | Bolts |  |  |  |  | 4 |  |  | B&F Fastener Supply | MPMS 003 0005 PH | 400 |  | MPMS 003 0005 PH

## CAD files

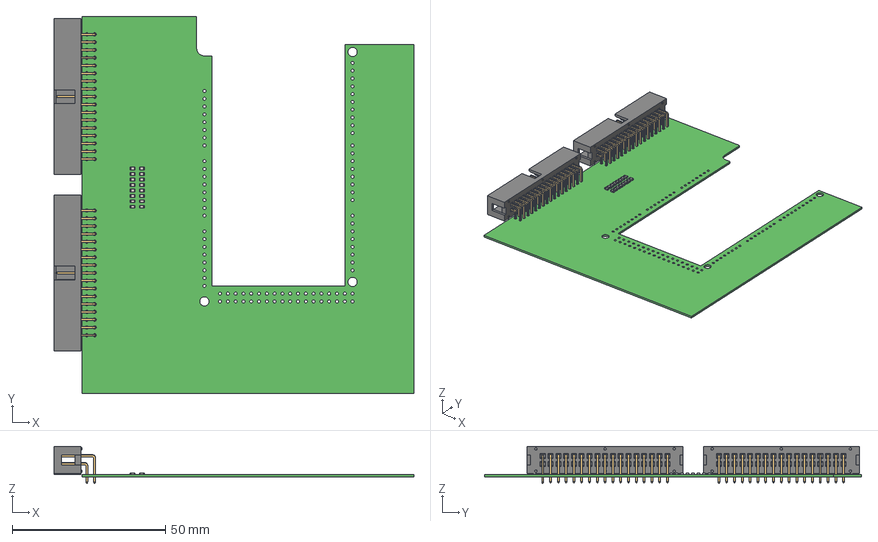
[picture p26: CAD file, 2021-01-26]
PCB_DueAdapter/PCB_DueAdapterL2/DueShieldL2.step
117.3 x 122.8 x 12.1 mm
Board
6120xx21721_PIN x 34
6120xx21721_PIN_LONGUE x 34
Extruded x 48

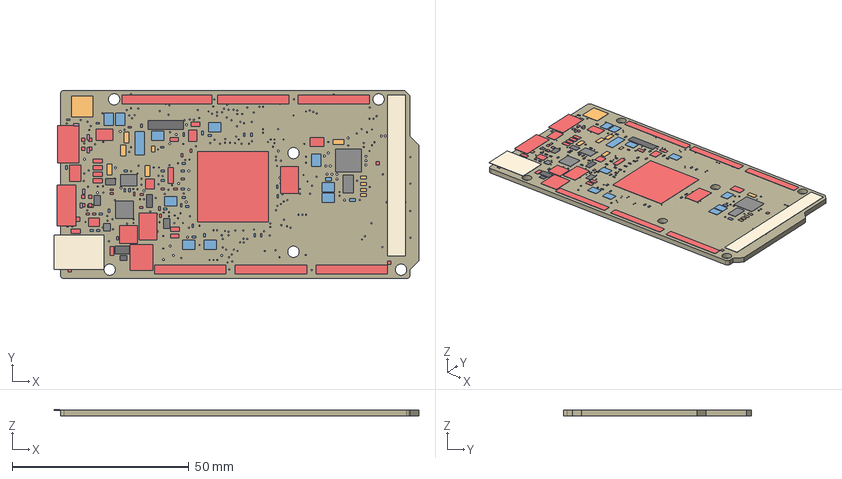
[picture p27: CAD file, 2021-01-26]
PCB_DueAdapter/PCB_DueAdapterL2/DUE_V02g.step
103.4 x 53.3 x 1.77 mm
Board
ICSP x 2
FH254-108DF08500V x 5
FH254-110DF08500V
47uF
Yellow x 6
POWER-SUPPLY
FIDUCIALMOUNT x 4
MF-MSMF050-2 500mA x 2
PMV48XP x 3
100nF x 32
1K5 x 5
TS42
18x2F-H8.5
LMV358IDGKR
32,768Khz_SMD
NX1117CE33Z
BRNCG0603MLC-05E x 5
56k x 6
16Mhz-KX-7 x 2
MH2029-300Y x 5
NM
100k x 19
22uF x 10
ATSAM3X8EA-AU
157SW
BC847B
MCR-AB1-S-RA-SMT-TR
ATMEGA16U2-MU
2x2M - NM
CD1206-S01575
74LVC1G125DCKR
SS1P3L
MSS1P3L-M3/89A
PINHEAD-2x5-P1.27
100nF_1 x 2
MPM3610
MCR-B-S-RA-SMT-CS1TR
PH1X4-THT
DNP x 8

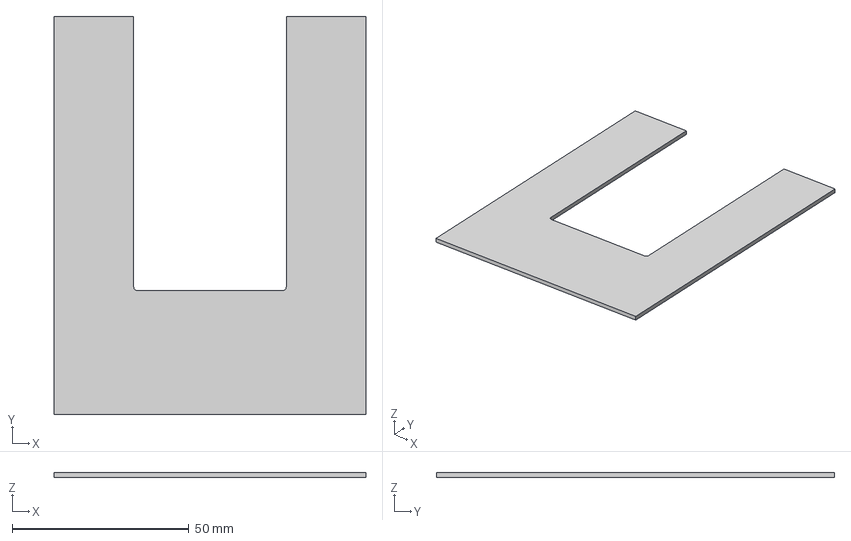
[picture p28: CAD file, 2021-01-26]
PCB_DueAdapter/PCB_DueAdapterL2/DUE_Adapter v2.step
88.3 x 112.7 x 1.50 mm

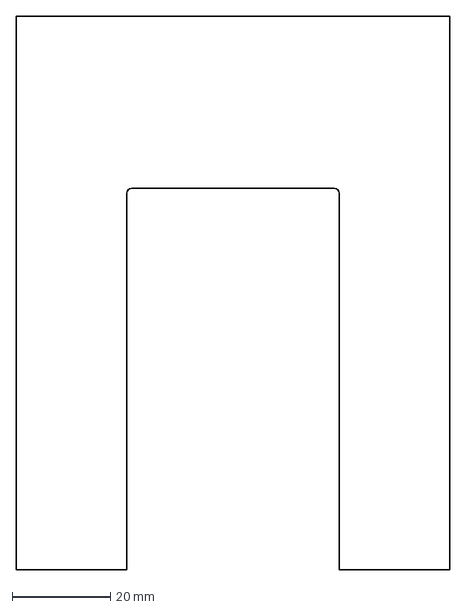
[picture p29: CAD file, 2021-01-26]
PCB_DueAdapter/PCB_DueAdapterL2/DUEBoardAdapter.dxf
88.3 x 112.7 mm

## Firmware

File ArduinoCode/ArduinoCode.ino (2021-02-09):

/* clang-format off */
// https://forum.arduino.cc/index.php?topic=453208.0
// https://ww1.microchip.com/downloads/en/DeviceDoc/Atmel-11057-32-bit-Cortex-M3-Microcontroller-SAM3X-SAM3A_Datasheet.pdf
// https://github.com/ivanseidel/DueTimer

#include <PID_v1.h>
#include <DueTimer.h>

bool loopTimeFlag = false;

struct pressureSensor_t {
	int pin;
	double zero;
	double scale;
};

const int numSensors = 2;
pressureSensor_t pressureSensor[numSensors] = {};

double setpoint, input, output;
double Kp = 1;
double Ki = 0;
double Kd = 0;
PID myController(&input, &output, &setpoint, Kp, Ki, Kd, DIRECT);

//struct controllerParams{
//	double setpoint, input, output;
//	double Kp;
//	double Ki;
//	double Kd;
//};
//PID controller();


void setup() {
  // Open a serial port
  Serial.begin(115200);
  
	// PWM set-up on pins
	// | PC3  | D35 | P1   |
	// | PC5  | D37 | P2   |
	// | PC7  | D39 | P3   |
	// | PC9  | D41 | P4   |
	// | PA19 | D42 | P5   |
	// | PC18 | D45 | MTR  |
	REG_PMC_PCER1 |= PMC_PCER1_PID36;  // Enable PWM

	REG_PIOA_ABSR |= PIO_ABSR_P19;  // Set the port A PWM pins to peripheral type B
	REG_PIOC_ABSR |= PIO_ABSR_P3 | PIO_ABSR_P5 | PIO_ABSR_P7 | PIO_ABSR_P9 | PIO_ABSR_P18;  // Set the port C PWM pins to peripheral type B

	REG_PIOA_PDR |= PIO_ABSR_P19;
	REG_PIOC_PDR |= PIO_ABSR_P3 | PIO_ABSR_P5 | PIO_ABSR_P7 | PIO_ABSR_P9 | PIO_ABSR_P18;  // Set the port C PWM pins to outputs

	REG_PWM_CLK = PWM_CLK_PREA(0) | PWM_CLK_DIVA(1);  // Set the PWM clock A rate to 84MHz (84MHz/1)

	// Loop for each PWM channel (6 in total)
	for (uint8_t i = 0; i < PWMCH_NUM_NUMBER; i++){
		PWM->PWM_CH_NUM[i].PWM_CMR = PWM_CMR_CPRE_CLKA;  // Enable single slope PWM and set the clock source as CLKA
		PWM->PWM_CH_NUM[i].PWM_CPRD = 2100;  // Set the PWM period register 84MHz/(40kHz)=2100;
	}

	REG_PWM_ENA = PWM_ENA_CHID5 | PWM_ENA_CHID4 | PWM_ENA_CHID3 | PWM_ENA_CHID2 | PWM_ENA_CHID1 | PWM_ENA_CHID0; // Enable all PWM channels

	// Loop for each PWM channel (6 in total)
	for (uint8_t i = 0; i < PWMCH_NUM_NUMBER; i++){
		PWM->PWM_CH_NUM[i].PWM_CDTYUPD = 1050;  // Set the PWM duty cycle to 50% (2100/2=1050) on all channels
	}

	pressureSensor[0]  = {A0, 406, 1600.0/1024.0};
	pressureSensor[1]  = {A1, 406, 1600.0/1024.0};
//	pressureSensor[2]  = {A2, 406, 1600.0/1024.0};
//	pressureSensor[3]  = {A3, 406, 1600.0/1024.0};
//	pressureSensor[4]  = {A4, 406, 1600.0/1024.0};
//	pressureSensor[5]  = {A5, 406, 1600.0/1024.0};
//	pressureSensor[6]  = {A6, 406, 1600.0/1024.0};
//	pressureSensor[7]  = {A7, 406, 1600.0/1024.0};
//	pressureSensor[8]  = {A8, 406, 1600.0/1024.0};
//	pressureSensor[9]  = {A9, 406, 1600.0/1024.0};
//	pressureSensor[10] = {A10, 406, 1600.0/1024.0};
//	pressureSensor[11] = {A11, 406, 1600.0/1024.0};

	myController.SetOutputLimits(0, 2100);
	myController.SetSampleTime(1);

  setpoint = 60; //kPa
//  controllerParams it = {0, 0, 0, 0, 0, 0};
//  PID *controller = new PID(&it.input, &it.output, &it.setpoint, it.Kp, it.Ki, it.Kd, DIRECT);

	// Setup a loop time for the controllers
	DueTimer loopTime = DueTimer(1);
	loopTime.attachInterrupt(loopTimeHandler).setFrequency(100).start();
}

void loop() {
	while(loopTimeFlag){
		// Wait for the loop to expire
	}

	input = analogToKpa(pressureSensor[0], analogRead(pressureSensor[0].pin));
	myController.Compute();
	setPWMDutyCycle(0, output);

	// Trigger the EOL condition
	loopTimeFlag = true;
}

double analogToKpa(pressureSensor_t sensor, int input){
	return((input - sensor.zero)*sensor.scale >= 0 ? (input - sensor.zero)*sensor.scale : 0);
}

void setPWMDutyCycle(int channelNumber, double value){
	PWM->PWM_CH_NUM[channelNumber].PWM_CDTYUPD = value;
}

void loopTimeHandler(){
	if(!loopTimeFlag){
		// Loop too long, probs print something
    Serial.println("Loop time exceeded");
		loopTimeFlag = false;
	}
}

// TODO thinking of making a class for a PID controller that either extends the normal arduino PID class or overwrites it. 
// This class would be of type "controllerPID" and allow the user to set a loop time etc


// TODO can you make an electron app or otherwise that you can interface with the arduino to give you real time feedback with dials and sliders? 

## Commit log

2021-01-21 Adds connector example to pinout
2021-01-26 Adds PCB files to repo
    [AnalogSensors.SchDoc, DUEBoardAdapter.dxf, DUE_Adapter v2.step, DUE_V02g.step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]
2021-02-08 Begins the arduino fun
2021-02-10 Remove some old files
    [PCB_IC.xlsx, PCB_IC.~(45).PcbDoc]
2021-02-17 Updates vis
    [DefinedSignalCalculator.xlsx]
2021-03-02 Re format
    [DefinedSignalCalculator.xlsx]
2021-05-01 Fixes pin names
2021-08-29 Fixes arduino 3.3V sensor inputs
    [AnalogSensors.SchDoc, DueShieldL2.PcbDoc, TopSheet.SchDoc]
2024-04-11 Adds pneusord to microlab box adapter
    [Main.GBL, Main.GBP, Main.GBS, Main.GKO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]

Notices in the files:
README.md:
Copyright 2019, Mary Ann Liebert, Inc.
